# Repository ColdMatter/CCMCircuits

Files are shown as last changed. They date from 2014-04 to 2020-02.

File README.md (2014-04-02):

CCMCircuits
===========

This is a repository for circuits used by the Centre for Cold Matter at Imperial College. Each project should be in its own directory, and should contain a .brd and a .sch file, a "readme.md" file which gives any useful information on the circuit. You can also upload files used to make the circuit in the PCB mill, and any measurements that you make of the circuit's behaviour. Please try not to upload all of the temporary files made by Eagle.

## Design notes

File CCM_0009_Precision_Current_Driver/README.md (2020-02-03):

# Precision Current Driver
     
This is a low-noise, low-current, bipolar-capable precision current supply.  Revision B onwards is modeled after Analog Devices application note AN-968.  Populate components as necessary to produce unipolar/bipolar operation with the desired input voltage to current scaling.

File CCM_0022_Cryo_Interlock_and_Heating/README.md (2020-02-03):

Cryocooler Interlock and Heating
===========

This circuit acts as a control interface and safety interlock for the F50 cryocooler compressor and system heaters for our usual buffer-gas beam configuration of three heater channels.  Both manual or remote control options are available.  The circuit only allows the compressor to be activated if the external (NC) interlock is satisfied.  The initial build of the YbF "box" chamber uses hardware interlocks (in series) on the chamber pressure and temperature of the first and second cooler stages.  Heater control is completely independent of the interlock.  Activation of either the first or second stage (but not the SF6) heaters will disable the cryocooler.

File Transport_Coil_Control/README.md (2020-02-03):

# Transport Coil Control
This is a controlling circuit for the large transport-coil pair used to tranfer CaF molecules from the MOT chamber into the dipole trap / optical tweezers chamber (and potentially also to the chip-trap chamber, the track is certainly long enough!).  We require full control of the coil pair, including the ability to switch between anti-Helmholtz and Helmholtz configurations, as well as the ability to fine tune to position of the field zero (vertically) by shunting current around the coils individually.  A simplified circuit schematic looks as follows.

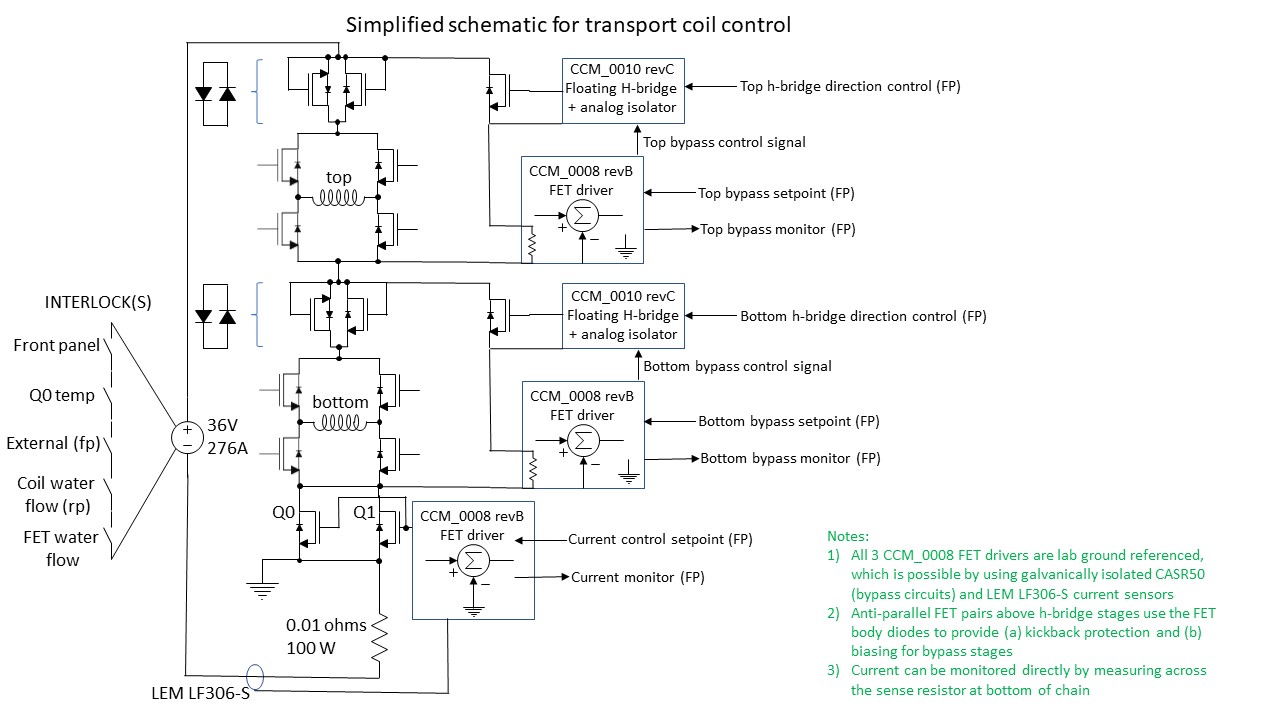
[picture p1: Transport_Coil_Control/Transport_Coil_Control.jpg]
Simplified schematic


Note that the connections to the 8 h-bridge FET gates are not shown.  

## Current sensor and control signal scaling/tuning
The control-voltage to output current conversion is set by adjusting the current monitor (indicator) voltage/current scaling.  The design of the FET-controlling feedback circuit CCM_0008 is such that the control voltage and monitor voltage differ by a factor of 2.  Namely, if the control voltage is 1V/A, the monitor signal will be 0.5V/A.

### Main current path/control
The LEM LF306-S current sensor is a closed-loop Hall sensor that provides a sensor current proportional to the sensed current in the ratio 1:2000.  Explicitly, a 300 A current will give an output of 150 mA.  Using a 33 ohm sense resistor, this gives a sensor voltage of 4.95V/300A.  To get the desired 1V/50A monitor scaling, we need a further gain of 1.212.  The instrumentation amplifier used in the monitor loop is the AD8226, with the gain set according to Rg (kOhms) = 49.4 kOhms / (G-1).  For our desired gain, we need a 232.8 kOhm resistor.  232 kOhms is close enough.  The resulting control voltage to output current scaling differs by a factor of 2, i.e. 1V/25A, or 25A/V.

### Bypass current path/control
The CASR50 sensors used for the two bypass circuits gives an output of 0.625V for the nominal current (50A).  We desire a monitor voltage of 1V/20A, i.e. a 50A bypass current gives a monitor voltage of 2.5V.  Thus, we want gain G = 2.5/0.625 = 4.  To get this gain for the AD8226, the gain resistor should be 16.46 kOhms.  16.5 kOhms is close enough.  The resulting bypass control voltage to output current scaling is half that of the monitor, i.e. 1V/10A, or 10A/V.  

<!-- h<sub>&theta;</sub>(x) = &theta;<sub>o</sub> x + &theta;<sub>1</sub>x -->

## Power supply remote control and monitoring
The current control box includes remote on/off, indicator leds, and signals from the Meanwell RTS-10000-36 high-current supply.  

### Connections and cabling 
The interface to the supply is achieved through three rear-panel connectors called CN991, CN992, and CN993, which are 20 pins, 10 pins, and 10 pins, respectively (HRS DF11-XYDP-2DS connectors, where XY = 10 or 20).  The signals of CN992 and CN993 are connected internally.  I've hacked a commercial DB15 cable to facilitate connecting to the power supply.  The connections are as follows:      

| RTS-10000-36 signal  | rear panel pin | Cable wire color | DB15 position |
| -------------------- | -------------- | ---------------- | ------------- |
| RC+                  | CN992 p10      | pinkish brown    | 1             |
| 12V-AUX              | CN991 p1       | red              | 2             |
| GND-AUX              | CN991 p3       | orange           | 3             |
| DC-OK2               | CN991 p4       | pink             | 4             |
| +V                   | CN991 p5       | yellow           | 5             |
| AC-FAIL2             | CN991 p8       | green            | 6             |
| -V                   | CN991 p7       | cyan             | 7             |
| OTP2                 | CN991 p9       | blue             | 8             |
| FAN-FAIL2            | CN991 p10      | light blue       | 9             |
| OTP1                 | CN991 p13      | purple           | 10            |
| DC-OK1               | CN991 p14      | grey             | 11            |
| AC-FAIL1             | CN991 p19      | white            | 12            |
| FAN-FAIL1            | CN991 p20      | black            | 13            |
| -                    | -              | brown + black    | 14            |
| -                    | -              | red + black      | 15            |
|                      |                |                  |               |

Note that the error/status signals are duplicated in two, electrically independent, channels.  Error signal X1 (e.g. fan-fail1) is a relay contact that closes to indicate failure (connects to fan-fail1-gnd).  Error signal X2 (e.g. fan-fail2) is an open-collector output that accomplishes the same functionality.  I've wired the control box in a way such that either of the two duplicated signals should trigger the indicator led (see below). 

There are also a number of connections to be made locally on the rear panel of the power supply.  Most of these simply connect the status indicator signals to system ground (GND-AUX).  The two exceptions are the output sense feedback, i.e. (CN992 p3 <--> output +) and (CN992 p5 <--> output -).  The ground connections are as follows (local brown wires daisy-chained to GND-AUX on CN991 p3).

| RTS-10000-36 signal  | rear panel pin |
| -------------------- | -------------- |
| RC-                  | CN992 p8       |
| DC-OK2-GND           | CN991 p2       |
| GND-AUX              | CN991 p3       |
| AC-FAIL2-GND         | CN991 p6       |
| OTP2-GND             | CN991 p11      |
| FAN-FAIL2-GND        | CN991 p12      |
| OTP1-GND             | CN991 p15      |
| DC-OK1-GND           | CN991 p16      |
| FAN-FAIL1-GND        | CN991 p18      |
| AC-FAIL1-GND         | CN991 p17      |
|                      |                |

### Remote on/off and interlocks 
The remote on/off control of the power supply is described in its datasheet.  Basically, RC- is connected to GND-AUX and RC+ is connected to 12V-AUX to enable the supply.  We use this as an interlock to enable/disable the supply for water flow and temperature conditions.  All of the following interlocks must be wired closed to enable the supply:

1. Rear panel BNC connector for transport coil water flow and temperature interlock.  If using a polarity-dependent interlock switch (e.g. a FET), the center pin is at higher electrical potential.

2. Front panel BNC connector for optional external interlock.  If using a polarity-dependent interlock switch (e.g. a FET), the center pin is at higher electrical potential.

3. Front panel on/off switch.

4.  Internal cooling water flow (can be manually defeated with internal jumper).  Note that the flow is directional in order to satisfy the interlock.

5. Main controlling FET (parallel pair consisting of Q0/Q1) source-terminal temperature.  Here, we use an AIRPAX normally-closed thermal switch, which opens at approximately 80 C.  

For the flow interlocks, we are currently using the Gems Sensors FS-3 (RS Components #3956940), which closes at a relatively low flow of 0.2 liters/minute.  If any of the interlock conditions are not met, the orange interlock indicator LED on the front panel should illuminate.  The interlock LED driving circuit is as follows.

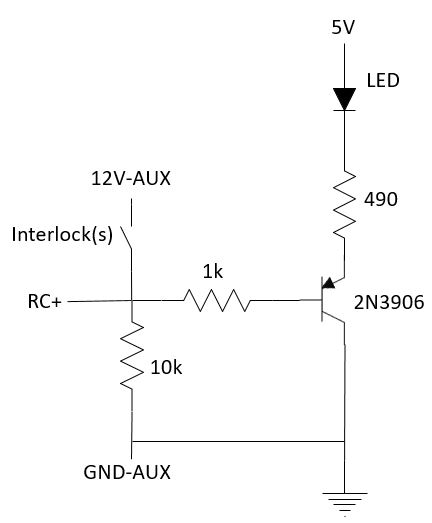
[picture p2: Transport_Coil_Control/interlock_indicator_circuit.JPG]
interlock circuit


### Status indicator leds/circuits
The status signals from the power supply are severly limited in terms of the available output current.  For this reason, I used these signals to drive a few basic transistor circuits that switch the front panel LED indicators on/off.  The LED-drive current itself is derived from the local 5V supply.  The four status indicators are driven by the following circuit.

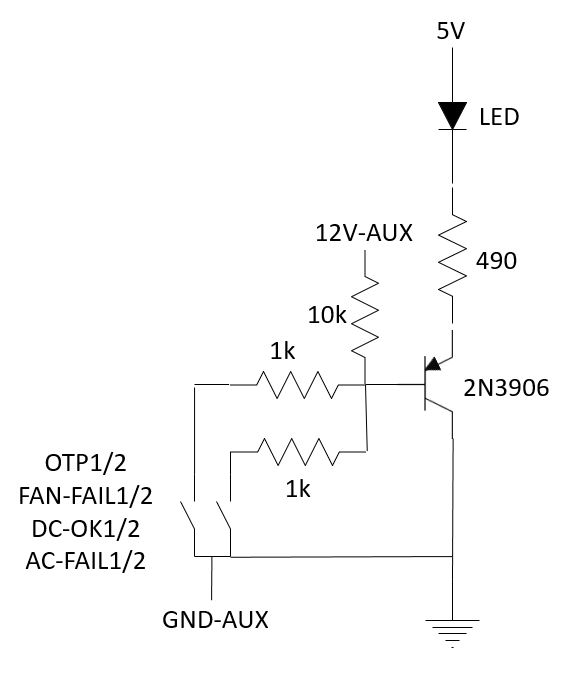
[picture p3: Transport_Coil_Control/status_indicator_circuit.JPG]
status circuit


To indicate a particular status is active, the supply closes an indicator relay that connects the output signal to GND-AUX.  This turns on the pnp BJT ('3906) and activates the LED.  Note that if the supply is not connected, 12V-AUX will not be present and all of the front-panel leds will be lit up.  

## Known Issues

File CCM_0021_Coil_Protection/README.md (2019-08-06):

# CCM_0021 Coil Protection
     
This circuit is designed to provide some level of protection for coils, particularly useful for those installed in vacuum where a melted coil represents a serious annoyance.  It features an adjustable soft current limit (by clamping a control voltage) and an adjustable hard energy limit (by opening an interlock and disabling the power supply).  The latter feature is obtained by integrating the dissipated power (roughly) and comparing to a setpoint.  

## Design Resources

## Design Notes

## Known Issues

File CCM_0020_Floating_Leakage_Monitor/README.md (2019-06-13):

# CCM_0020 50kV Floating pA Leakage Current Monitor
     
This is a circuit used to monitor pA-level leakage currents on the HV plates of 
the ultracold edm experiment.  We have a design goal of having the leakage currents be less than 25 pA.  To make sure this is the case, we want to be able to measure currents at the pA level.  This is hard.  Floating the entire circuit up to a few tens of kV makes it even harder.  This is my kind of problem -NF.    

## Design Resources
- Bob Pease: What's all this teflon stuff anyhow?
- Bob Pease: What's all this femtoampere stuff anyhow?
- Keithley low-level measurement handbook
- LM662 datasheet
- Analog Devices ADA4530-1 datasheet: https://www.analog.com/media/en/technical-documentation/data-sheets/ADA4530-1.pdf 
- Analog Devices ADA4530-1 demo board user's guide: https://www.analog.com/media/en/technical-documentation/user-guides/ADA4530-1R-EBZ_UG-865.pdf

## Design Notes
The transmitter section of the circuit features three critical design elements: 
ultra low input leakage currents, ultra low power consumption, and high voltage 
isolation.  The former is required of any circuit capable of measuring currents 
on the pA level.  The most sensitive way to measure extremely low currents (like the fA-level features by some of the op amps we'll be using here) is to integrate for many seconds and read off the voltage.  Of course, you need an integrating capacitor with low leakage too: a length of teflon coated coaxial wire is a good choice, you can even drive the coax outer conductor with a shielding potential ("self shielded") to avoid dielectric relaxation effects.  The small enclosed volume also lowers the sensitivity to cosmic rays, to which you are sensitive to at this level.  To monitor the leakage on the edm electric field plates, we need a time-resolved signal, so integrating is out.  We don't care at the fA level, so this shouldn't pose a problem.  A sense resistor + buffer amplifier (alternatively, a transimpedance amplifier) should be sensitive enough and give us real-time measurements. 

Achieving ultra low input leakage currents starts with choosing an appropriate 
operational amplifier, in this case in a voltage "buffer" configuration.  Luckily, there are a number of (CMOS) op amps on the market that feature input leakage currents on the order of 10 fA.  We have the additional challenge of needing an op amp that has low quiescent current requirements.  The LMP2231 made by Texas Instruments seems to fit the bill: 20 fA input leakage current (typical, 1 pA max) while only needing 10 uA of quiescent current.

Taking advantage of the ultra-low input current leakage specification of our chosen op amp requires a significant amount of layout/design work.  It won't do us any good to use such an op amp on a dirty FR4 board that will leak currents of many pA into our inputs every time the humidity changes.  The first line of defense is to use a low-leakage circuit board material.  A 4-layer board with outer layers made of Rogers 4350B (a ceramic) and the inner substrate made of FR408 (for strength) seems like a good way to go.  Beyond that, high-impedance circuit inputs are shielded at numerous levels.  The buffer op amp inputs use a "guard ring" driven by a low impedance source (the op amp output) held at the same voltage as the inputs themselves, which eliminates leakage from surrounding on-board potentials.  The guard ring is exposed copper so that no charge carriers can leak past on the soldermask or silkscreen layers.  The guard ring extends underneath the top ceramic layer to shield the input pins (from below) from the FR4 inner layer.  A via fence on the outer perimeter of the guard ring completes the board-level shielding.  Additional shielding is achieved by two layers of brass boxes, the inner one (top and bottom of the board) at the same potential as the guard ring and the outer one (again, on both top and bottom) at floating "ground".  A triax cable uses the same two shielding potentials to bring the HV line into the circuit.

Of all the challenges to overcome here, the HV isolation is perhaps the easiest to overcome.  Optek makes the OPI15X series of opto-couplers/isolators that are rated to 50 kV in air.  We could just do our usual trick: use a sense resistor and buffer amplifier to generate a voltage, convert that voltage to a frequency using a VtoF converter and optically transmit that frequency.  Optical transmission can either be done using a fiber (e.g. Agilent's HFBR-1520) or an Optek OPI155 optoisolator.  However, both of these require significant (many mA) led drive current in order to toggle the logic output on the receiver.  Instead, I'm planning to use the OPI150 optocoupler (transmitting LED + receiving phototransistor) with the phototransistor receiver wired as a photodiode (base shorted to emitter) and the generated photocurrent being detected by a high-gain transimpedance amplifier.  In principle, this should allow us to get the signal out using much less power.  The output of the transimpedance could even feed into a precisely tuned comparator to give high sensitivity and logic-level outputs.  We could even transmit an analog signal instead of a digital one using the same setup but without the receiver comparator.  I think the digital approach will have better noise immunity, larger dynamic range, and potentially uses less power.  That means we'll likely have to do VtoF after all.  Even though you can't buy low power VtoF ICs (or VCOs), you can build your own.  The LTC1541 [op amp + comparator + voltage reference] has one option in the applications section of its datasheet.  You can build a 0-10 kHz VtoF with quiescent current requirements around 5 uA, some 200 x less than the lowest power monolithic solution.  

Along with the problem of high-voltage isolation comes the question of how to power the isolated transmitter section of the circuit.  The most obvious answer is to use batteries, but in practice that turns out to be relatively annoying.  An alternative is to power the circuit using some high-power leds and a solar panel on the transmitter.  This sounds elegant, and I think it probably could be if the transmitter was designed for very low-power operation, but in practice it makes the current monitors very big (and bright -- you need lots of optical power).  I've decided to try something crazy: design for ultra-low power on the transmitter and power it via photocurrent generated from (many of)
the same model of optocoupler that we're using to get the signal out.  With a max allowed LED current of 50 mA and a transfer ratio of ~2000:1, with six optocouplers I think I should be able to create a 2.5 V, 50 uA power supply on the transmitter circuit.  With a careful design I think that should be enough. 

## Known Issues

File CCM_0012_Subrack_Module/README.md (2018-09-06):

# CCM_0012 Subrack Module

This is meant to be the starting point for any circuit/project that will be inserted into a subrack using the standarized CCM bus (see CCM_0011).  Standard board sizes are 160 x 100 mm.

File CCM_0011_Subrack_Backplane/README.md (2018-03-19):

Subrack Backplane
===========
     
This circuit is an attempt to create a subrack standard for CCM circuits.  It uses a 64-pin bus based on the EURO-card standard (100 mm tall boards x various lengths, typically 160 mm) using DIN41612 "Type B" connectors.  The bus provides separate analog and digital ground planes and associated power supplies of +/-15V and +/-5V, respectively.  The backplane provides female connectors with a 4HP pitch.

We have a number of existing circuits that use a 32-pin rear connector (actually a 64-pin connector with half of the pins unpopulated).  The bus standard defined here should be compatible with our existing circuits.

In addition to power rails, the backplane also provides various communication buses, which can be used with microcontroller projects.  Take care though, the GPIOX and ANX lines are shared across all daughter boards, which can cause conflicts if you aren't careful.  In a similar vein, please only install a single power-supply module!

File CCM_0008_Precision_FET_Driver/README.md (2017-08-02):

Coil Driver
===========
     
This circuit provides closed-loop control of either unipolar or bipolar power current-driver output stages.

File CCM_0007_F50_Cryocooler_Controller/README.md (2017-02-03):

Cryocooler Phase Lock
===========

This project is meant to allow us to phase lock our buffer-gas molecular beam experiments to the ~ 1 Hz cryocooler cooling cycle.  It accomplishes this placing a microphone close to the high-pressure helium lines and providing an output trigger based on when the volume exceeds some threshold.  The delay can be controlled with an analog input.

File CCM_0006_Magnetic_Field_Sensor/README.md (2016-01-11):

# CCM_0006 Magnetic field sensor

This is a battery-powered circuit designed to help measure the strong magnetic fields produced by the Zeeman-Sisphus decelerator magnet arrays.  The circuits consists of a single-turn pickup coil (copper trace), and RMS-to-DC converter, summer, and VtoF converter.  The idea is to spin the circuit (using something like the dremmel tool) with the pickup coil in the bore of the magnet arrays.  The LED will flash at a frequency proportional to the field strength and the output signal can be picked up on a photodiode.  Both the rotation rate and magnetic field strength should be able to be derived from the photodiode pickup signal.

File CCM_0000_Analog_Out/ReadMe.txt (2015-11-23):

This is a simple analog output board useful for providing an adjustable voltage to a pzt amplifier, cavity, etc.  Jumpers allow the user to choose between unipolar and bipolar operation.  Substituting various LM-4040 (or equivalent) reference diodes allows the voltage ranges to be adjusted.  

Currently, everyone in the lab uses 9V batteries with old-school trimpots wired up to them for this type of application.  Unsurprisingly, nobody ever remembers to disconnect the battery when they are finished.  As a result, we have lots of dead 9V batteries in the lab.  I've remedied the problem temporarily with some rechargeable batteries, but the practice is still stupid.

It might be a better idea to do a multi-channel board that fits nicely in a NIM rack...

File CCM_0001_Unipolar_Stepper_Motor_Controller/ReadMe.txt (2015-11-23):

To configure a blank board, flash the PIC and run the FTDI chip configure batch file/utility (ftdi/stepper_ftdi_config.bat).

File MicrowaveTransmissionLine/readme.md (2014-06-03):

Microwave transmission line		
=====================
A short section of 50 ohm parallel plate transmission line for 14.5GHz microwaves, with two feedthroughs.

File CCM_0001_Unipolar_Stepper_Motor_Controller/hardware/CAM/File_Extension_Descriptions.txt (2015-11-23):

Extension Description

.cmp copper top (component) side
.drd	drill 
.dri drill station info
.gpi photoplotter info file
.plc silk screen top (component) side
.pls silk screen bottom (solder) side
.sol copper bottom (solder) side
.stb stencil file bottom (solder) side
.stc solder stop mask top (component) side
.sts solder stop mask bottom (solder) side
.stt stencil file top (component) side

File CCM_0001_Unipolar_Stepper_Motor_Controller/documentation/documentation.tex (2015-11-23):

\documentclass[10pt]{article}
\usepackage{amsmath,graphicx,xcolor,tikz,amssymb,multirow}
\usepackage[final]{pdfpages}
\usepackage{hyperref}
\usepackage{empheq}
\usepackage{fancyhdr}
\usepackage{textcomp}
\usepackage{placeins}
\usepackage{url}

\newcommand{\HRule}{\rule{\linewidth}{0.5mm}}

\newcommand{\comm}[3]{
\nonumber \textcolor{red}{?} \, \textcolor{blue}{!} \, \textcolor{red}{\text{ #1}} \,\textcolor{red}{\text{#2, }} \, \textcolor{blue}{\text{AOK.}} \, & \text{\hspace{0.5in}#3}}

\newcommand{\exchange}[2]{
\begin{equation}
 \nonumber \textcolor{red}{?} \, \textcolor{blue}{!} \, \textcolor{red}{\text { #1}} \,\textcolor{red}{\text{#2, }} \, \textcolor{blue}{\text{AOK.}}
 \end{equation}
}

\newcommand{\exchangeWithData}[2]{
\begin{equation}
 \nonumber \textcolor{red}{?} \, \textcolor{blue}{!} \, \textcolor{red}{\text { #1}} \,\textcolor{red}{\text{#2, }} \, \textcolor{blue}{data1,data2,...} \, \textcolor{blue}{AOK.}
 \end{equation}
}

\pagestyle{fancy}
\lhead{{\large Stepper Motor Controller}}
\rhead{}
\chead{}
\lfoot{{\large Imperial College CCM \the\year}}
\rfoot{\large Page \thepage}
\cfoot{}
\setlength{\headheight}{14pt} 
\renewcommand{\headrulewidth}{0.4pt}
\renewcommand{\footrulewidth}{0.4pt}

\begin{document}
\input{./title.tex}

\newpage
\tableofcontents

\newpage
{\large{\bf Known Issues}}
\begin{enumerate}
\item{Somehow I forgot to put a pullup resistor on the $\overline{\text{MCLR}}$ line of the PIC.  In order to operate, put a 10k$\Omega$ pullup resistor to 5V.  Just under the programming connector is a convenient place (0603/0805 between that and the adjacent pin).}
\end{enumerate}

\vspace{0.5in}

{\large{\bf Minimum Requirements}}
\begin{enumerate}
\item{If using the provided GUI, you will need windows XP or newer (system has only tested on Windows 7).}
\item{If PC control/interaction with the controller is desired, you must at the very least have the FTDI COM port drivers installed.  These are included in the gui installation executable.}
\end{enumerate}

\FloatBarrier
\newpage
%%%%%%%%%%%%%%%%%%%%%%%%%%%%%%%%%%%%%%%%%%%%%%%%%%%%%%
%%%%%%%%%%%%%%%%%%%%%%%%%%%%%%%%%%%%%%%%%%%%%%%%%%%%%%%
\section{System Overview}
This circuit and associated firmware/software act as a controller for a standard unipolar (6 wire) stepper motor.  The rotary position of the motor can be controlled from a usb connection using a simple serial protocol, or with the provided gui.  In addition, a number of potentially useful predefined operation modes are available for controlling the motor.  The hardware also includes a rotation sensor, making possible both open and closed-loop operation.

All files and folders discussed in this documentation are located in the \url{CCM_0001_Unipolar_Stepper_Motor_Controller\\RevA} directory.  File and folder paths referenced herein are described \emph{relative} to this location.

%%%%%%%%%%%%%%%%%%%%%%%
\subsection{Hardware}
\label{Hardware}   
The heart of the controller is a PIC18F46K80, with a number of peripherals to facilitate motor control.  These include a DS3231M real time clock, 24AA1025 external eeprom, HCTL-2021 quadrature encoder, AMT102 rotation sensor, L297 motor driver, and power FETs for the output drive stages.  Two external bnc inputs (trigger and direction control) and two pushbuttons facilitate control of the motor by the user in various operation modes.  An LCD screen provides visual feedback of motor behaviour to the user. 

The motor used for the purpose of this documentation, and that which was used in the initial builds of the prototype circuits, is part number 191-8299 from RS components.  This is a 12V, 0.4A/phase 1.8$^\circ$/step motor.  The motor runs quite hot when supplied with the full specified voltage, for this reason the prototypes were built using a 7.5V supply instead.  The lower supply voltage sacrifices a bit of switching speed and torque but otherwise has no adverse consequences.  With these operating parameters, the fasted stepping rate is on the order of 500 Hz.  Stepping speed performance and reliability is load dependent and should be tested for the particular applications.         

%%%%%%%%%%%%%%%%%%%%%%%
\subsection{Open vs. Closed Loop Operation}
\label{Open_vs_Closed} 
Although probably not needed for most applications, the controller can be operated in closed-loop mode.  When operated this way, the current position of the motor is determined by the AMT-102 rotation sensor, rather than by how many steps the controller has instructed it to take.\footnote{The rotation sensor is set to output 800 quadrature encoded pulses per rotation.  The quadrature encoder used multiplies this by 4 so we get 16 counts for every step of the motor.}  When operated closed-loop, the controller will attempt to make this position equal to the desired position (determined by the number of triggers received in external mode, or where it thinks the motor should be in other modes).  Closed-loop operation will probably be most useful in situations where the load torque is significant, which can cause the stepping motor to ``slip'', i.e. not actually take a step even though the controlling currents toggled correctly.  If it is crucial that the motor position be accurate, it is recommended to use closed-loop mode.    

\FloatBarrier
\newpage
%%%%%%%%%%%%%%%%%%%%%%%%%%%%%%%%%%%%%%%%%%%%%%%%%%%%%%%%%
%%%%%%%%%%%%%%%%%%%%%%%%%%%%%%%%%%%%%%%%%%%%%%%%%%%%%%%%%
\section{GUI} 
\label{GUI}    

In addition to the developed firmware and hardware, there is also a provided GUI that facilitates control of the motor position and configuration of the predefined operation modes.  The GUI itself was written in Labview, which is horrible of me I know.  However, this was based on an old project and I didn't see the value in re-inventing the wheel there.    

The controller system can be installed by running
\url{gui\\Installer_Builds\\Volume\\setup.exe}.  This will carry out installation of the gui, FTDI device drivers, and Labview runtime engine.  A shortcut to the gui executable will be created on your desktop.  Updates of the gui can be carried out by simply replacing the executable itself, there is no need to rerun the entire installer.

When the gui executable is run, the first thing the back end code will do is search for a controller on the specified COM port.  The result of this test is indicated with the ``Controller Detected?'' LED.  Each time a button is depressed, and an action is taken, the ``Task Completed?'' LED will indicate the success (or lack thereof) of carrying out the desired operation.  For tasks that take a long time to execute, such as a goto, this LED will blink yellow while the task is carried out.  Explicit views of the data sent to and returned from the controller are shown in the two boxes to the left of the tab control.  Responses of AOK typically indicates the command was received and executed successfully.  ERR will indicate there was an error.  

%%%%%%%%%%%%%%%%%%%%%%%%%%%%%%%%%
\subsection{Basic Operation}
\label{Basic_Operation}
The basic operation tab of the controller gui allows for immediate control of the motor position (goto/move) as well as setting a number of operation variables.  These include uploading the current time, setting position limits, step rates, etc.    

\begin{figure}[!htb]
\centering
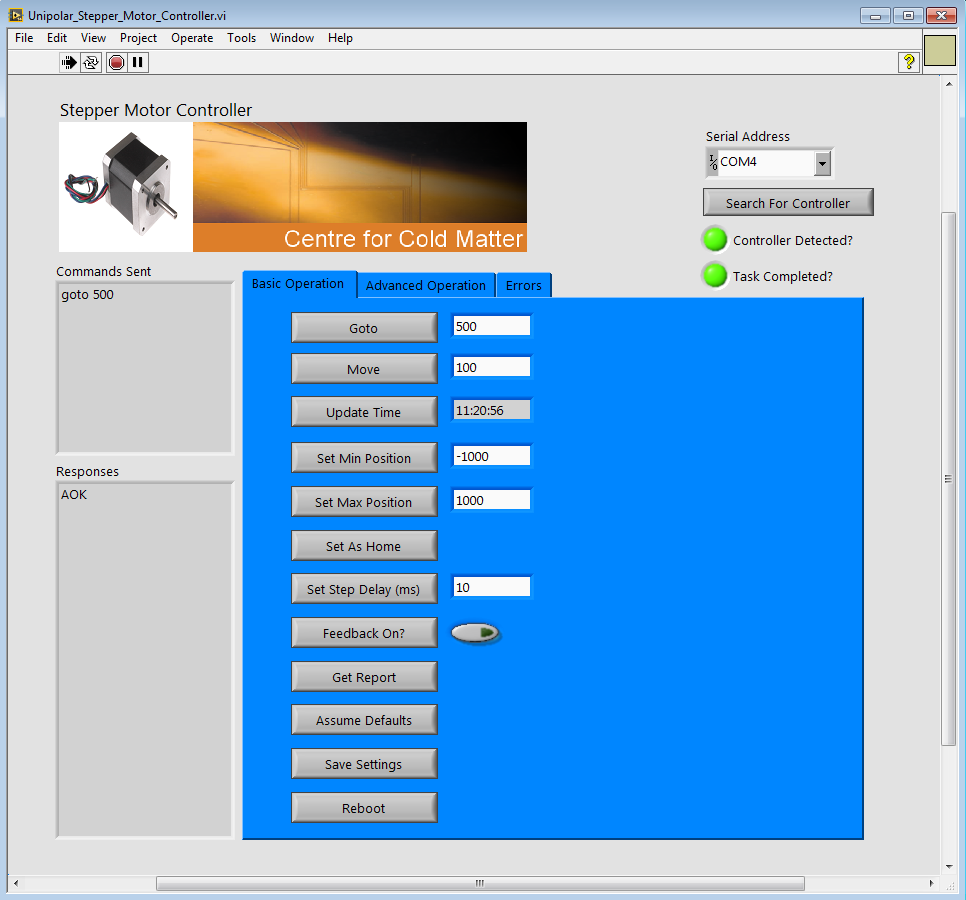
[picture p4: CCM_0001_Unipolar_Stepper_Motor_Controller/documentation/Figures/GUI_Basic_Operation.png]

\caption{Basic operation tab of the motor controller gui.}
\label{GUI_Basic_Operation}
\end{figure} 

\FloatBarrier
%%%%%%%%%%%%%%%%%%%%%%%%%%%%%%%%%
\subsection{Advanced Operation}
\label{Advanced_Operation}

The advanced operation tab (see Figure \ref{GUI_Advanced_Operation}) of the gui is used to configure the predefined operation modes native to the controller firmware.  Various configuration settings will be enabled/disabled, depending on the operation mode selected in the top dropdown menu.  The sequence of serial commands sent to the controller to configure the mode (in the Figure the triggered-goto mode has just been configured) is explained in detail in Section \ref{Configuring_Predefined_Operation_Modes}.  

\begin{figure}[!htb]
\centering
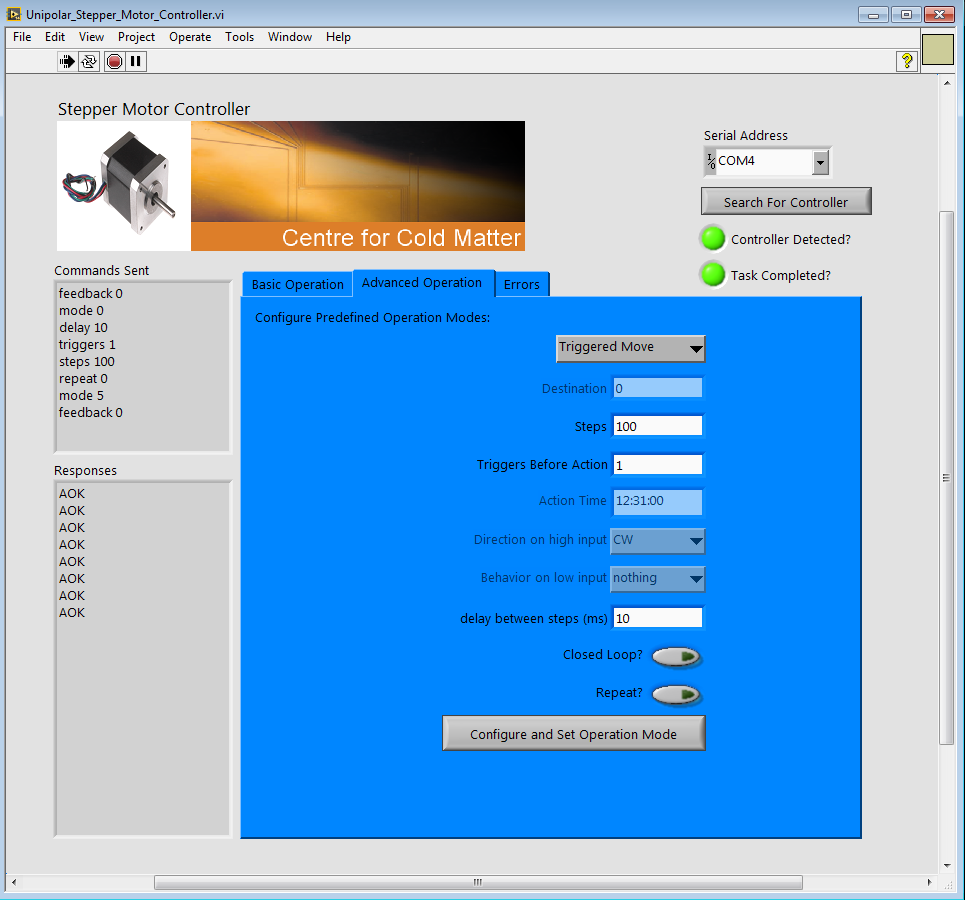
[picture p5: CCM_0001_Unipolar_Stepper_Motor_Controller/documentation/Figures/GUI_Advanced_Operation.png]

\caption{Advanced operation tab of the motor controller gui, used for configuring the predefined modes of operation.}
\label{GUI_Advanced_Operation}
\end{figure}

\subsubsection{Motor Disabled (0)}
In this mode the motor is disabled (stepping currents are turned off), allowing for free rotation.  

\subsubsection{Manual (1)}
In manual mode, the position of the motor is controlled using the two front-panel pushbuttons.  Push once to step the motor once, push and hold to continually rotate the motor.  

\subsubsection{External (2)}
In external mode, the stepping rate and direction of the motor are controlled by the two bnc inputs,  steps being taken on rising edges of the trigger input.  At the time of the rising edge of the trigger, the direction logic level determines if a positive (1) or negative (0) step is to be taken.  The direction logic input should be stable for at least $\pm$10$\mu$s around the rising trigger edge.  

\subsubsection{Triggered Goto (3)}
In triggered-goto mode, the controller is loaded with a goto destination and required number of triggers.  It then counts incoming triggers on the external bnc input (rising edges), the goto being completed when the desired number of triggers has been reached.  After completion, the controller automatically assumes manual mode.      

\subsubsection{Timed Goto (4)}
In timed-goto mode, the controller is loaded with a goto destination and action time.  The current time is monitored until a match is detected for hours/minutes/seconds, at which point the goto is completed.  After completion, the controller automatically assumes manual mode.  

\subsubsection{Triggered Move (5)}
In triggered-move mode, the controller is loaded with a step value and required number of triggers.  It then counts incoming triggers on the external bnc input (rising edges), the move being completed when the desired number of triggers has been reached.  Behaviour after the move is determined by the ``repeat'' setting.  If true, the controller resets the trigger count and prepares to repeat the move procedure once the required number of triggers has again been reached.  If false, the controller assumes the manual operation mode.  

\subsubsection{Timed Move (6)}
In timed-move mode, the controller is loaded with a step value and action time.  The current time is monitored until a match is detected for hours/minutes/seconds, at which point the move is completed.  Behaviour after the move is determined by the ``repeat'' setting.  If true, the controller resets the trigger count and prepares to repeat the move procedure once the required number of triggers has again been reached.  If false, the controller assumes the manual operation mode.

\subsubsection{State-Based Rotation (7)}
In state-rotation mode, the controller continually rotates the motor.  The rotation direction is determined by the instantaneous state of the external ``trigger'' bnc input and the ``rotate'' and ``behave'' settings, as summarized in Table \ref{State_Rotate_Table}.  When the external trigger input is high, the rotation direction is determined by the rotate setting.  When low, the motor can either do nothing (behave=0), or anti-rotate (behave=1) against the normal ``external trigger is high'' direction.  No feedback is possible during this mode.    

\begin{table}
\centering
\begin{tabular}{|c|c|c|c|}
\hline
Ext Trigger & rotate & behave & motion \\
\hline
1 & 0 & - & negative rotation \\
\hline
1 & 1 & - & positive rotation \\
\hline
0 & - & 0 & no motion \\
\hline
0 & - & 1 & anti-rotate ($\overline{\text{rotate}}$)  \\
\hline
\end{tabular}
\caption{Motor control in the ``state rotate'' operation mode is controlled by a single external input (Ext Trigger) and two internally set bits (rotate and behave).}
\label{State_Rotate_Table}
\end{table}  

\subsubsection{Triggered Shutter (8)}
In the triggered-shutter mode, the controller waits for a number of triggers (rising edges on the external trigger input) before moving the motor a specified number of steps, in effect ``opening'' a shutter.  The controller then resets the trigger count and waits for the same number of triggers before returning to the home position.  This mode repeats indefinitely.  

\subsubsection{State Shutter (9)}
In the state-shutter mode, the controller monitors the external trigger input and positions the motor in one of two places depending on the current logic state.  The direction and rotation amplitude is set by the ``steps'' variable.  This mode repeats indefinitely.  

\FloatBarrier
\newpage
%%%%%%%%%%%%%%%%%%%%%%%%%%%%%%%%%%%%%%%%%%%%%%%%%%%%%%%%%
%%%%%%%%%%%%%%%%%%%%%%%%%%%%%%%%%%%%%%%%%%%%%%%%%%%%%%%%%
\section{Serial Communication} 
\label{Serial_Communication}
In addition to the GUI, general operation and configuration of the individual predefined operation modes can be configured directly over a serial port connection.  This project uses a baud rate of 4800, 8 data bits, 1 stop bit, no port control, and no parity bit.

Each exchange between the host (PC) and the controller consists of the host giving the controller a task.  Task-dependent behaviour, including exchange of data or changing settings, can then take place.  The assignment and carrying out of each task follows a fixed protocol, as summarized in the following list. For clarity of discussion regarding communication between the host and controller, \textcolor{red}{red characters/data are sent from the host to the controller} and  \textcolor{blue}{blue characters/data are sent from the controller to the host}.   
  
\begin{enumerate}
\item{The wakeup ascii character \textcolor{red}{?} is sent to the controller to instigate communication.}
\item{When ready to receive the command, the controller returns \textcolor{blue}{!}.  If the wakeup characters was incorrect, the controller returns \textcolor{blue}{?} instead and aborts the operation.}
\item{The command, with required arguments, is sent to the controller.  If a command has arguments, the command and it's arguments are separated by a space.  The command/argument sequence terminates with a carriage return ascii character (CR, 0x13) or line feed (LF, 0x10).\footnote{Technically, \emph{any} non-alphabetic or numeric ascii character will work, other than a space.}}
\item{The controller carries out the specified task.}
\item{The controller ends the current task by sending "AOK" if the task was carried out without errors, or "ERR" if an error occurred, potentially with an error message, terminated by a line feed (LF, 0x10).}
\end{enumerate}

An example of adjusting settings on the controller from a serial port terminal (TeraTerm in this case) is shown in Figure \ref{Serial_Example}.  The terminal is setup to echo host keyboard entries to the screen.  As shown, each command begins with the exchange of ``?'' (sent by the host), with ``!'' returned from the controller.    

\begin{figure}[!htb]
\centering
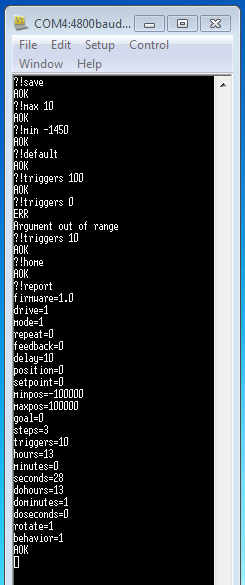
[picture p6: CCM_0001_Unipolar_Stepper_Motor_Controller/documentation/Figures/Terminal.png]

\caption{Example interaction with the controller over USB using individual commands sent from teraterm.}
\label{Serial_Example}
\end{figure} 

\FloatBarrier
%%%%%%%%%%%%%%%%%%%%%%%%%%%%%%%%%%%%%%%%%%
\subsection{Available Commands}

Available commands sent to the controller and brief description of the associated task are summarized in Table \ref{commands}.  The ``goto'' and ``move'' commands are used for immediate motor operation.  Some of the other commands are only used in certain operation modes.        

\begin{table}[!hb]
\centering
\begin{tabular}{|c|c|c|}
\hline
Command & 
Description & 
used in modes 
\\
\hline
\hyperref[report]{report} & 
report current settings &
-
\\ \hline
\hyperref[default]{default} & 
assume default values &
-
\\ \hline
\hyperref[save]{save} & 
save settings &
-
\\ \hline
\hyperref[home]{home} & 
set position as home &
-
\\ \hline
\hyperref[reboot]{reboot} & 
reboot the controller &
-
%\\ \hline
%\hyperref[update]{update} & 
%update firmware &
%-
\\ \hline
\hyperref[move]{move} & 
move the motor N steps &
-
\\ \hline
\hyperref[goto]{goto} & 
goto position &
-
\\ \hline
\hyperref[max]{max} & 
set maximum position &
all
\\ \hline
\hyperref[min]{min} & 
set minimum position &
all
\\ \hline
\hyperref[delay]{delay} & 
set delay between steps &
all
\\ \hline
\hyperref[feedback]{feedback} & 
set feedback on/off &
all
\\ \hline
\hyperref[mode]{mode} & 
set operation mode &
-
\\ \hline
\hyperref[steps]{steps} & 
set number of steps &
5,6,8,9
\\ \hline
\hyperref[triggers]{triggers} & 
set trigger events before action&
3,5,8
\\ \hline
\hyperref[goal]{goal} & 
set destination &
3,4
\\ \hline
\hyperref[hours]{hours} & 
set current time (hours) &
4,6
\\ \hline
\hyperref[minutes]{minutes} & 
set current time (minutes) &
4,6
\\ \hline
\hyperref[seconds]{seconds} & 
set current time (seconds) &
4,6
\\ \hline
\hyperref[dohours]{dohours} & 
set action time (hours) &
4,6
\\ \hline
\hyperref[dominutes]{dominutes} & 
set action time (minutes) &
4,6
\\ \hline
\hyperref[doseconds]{doseconds} & 
set action time (seconds) &
4,6
\\ \hline
\hyperref[repeat]{repeat} & 
set loop behaviour condition &
5,6
\\ \hline
\hyperref[rotate]{rotate} & 
set rotation direction for logic high input &
7
\\ \hline
\hyperref[behave]{behave} & 
set state-rotate behaviour for logic low input &
7
\\ \hline
\end{tabular}
\caption{Available commands to send to the controller from the host.}
\label{commands}
\end{table} 

Examples of the usage of each command in Table \ref{commands} appears below.  Some commands require arguments, while others do not.
In each example, commas (,) indicate carriage returns and periods (.) indicate line feeds.  

%%%%%%%%%%%%%%%%%%%%%%%%%
\subsubsection{report}
\label{report}
Instructs the controller to return a list of the current settings, each setting is of the format ``setting$=$value'', with a carriage return between each list entry. 

\exchangeWithData{report}{} 

%%%%%%%%%%%%%%%%%%%%%%%%%
\subsubsection{default}
\label{default}
Instructs the controller to restore default values. 

\exchange{default}{}

%%%%%%%%%%%%%%%%%%%%%%%%%
\subsubsection{save}
\label{save}
Instructs the controller to save the current settings.  These will be restored if the controller is reset.

\exchange{save}{}

%%%%%%%%%%%%%%%%%%%%%%%%%
\subsubsection{home}
\label{home} 
Instructs the controller to set the current position as home (0).

\exchange{home}{}
    
%%%%%%%%%%%%%%%%%%%%%%%%%
\subsubsection{reboot}
\label{reboot}
Carries out a restart of the controller equivalent to that during a hard power supply cycle.  The communication flow looks like:    

\exchange{reboot}{}

%%%%%%%%%%%%%%%%%%%%%%%%%
%\subsubsection{update}
%\label{update}
%Invokes the bootloader on the controller, in order to carry out a firmware update.  %This should be used in conjunction with the ds30 bootloader utilities, available in %the \url{bootloader\\ds30} directory.  The communication flow follows:    

%\exchange{update}{}

%%%%%%%%%%%%%%%%%%%%%%%%%
\subsubsection{move}
\label{move}
Moves the motor a specified number of steps. The number of steps must be between -2000000 and 2000000.         

\exchange{move}{-100}

%%%%%%%%%%%%%%%%%%%%%%%%%
\subsubsection{goto}
\label{goto}
Moves the motor to a specified position. The destination must be between -1000000 and 1000000.         

\exchange{goto}{1000}

%%%%%%%%%%%%%%%%%%%%%%%%%
\subsubsection{max}
\label{max}
Set the maximum allowed motor position, -1000000 to 1000000.         

\exchange{max}{10000}

%%%%%%%%%%%%%%%%%%%%%%%%%
\subsubsection{min}
\label{min}
Set the minimum allowed motor position, -1000000 to 1000000.         

\exchange{min}{-10000}

%%%%%%%%%%%%%%%%%%%%%%%%%
\subsubsection{delay}
\label{delay}
Set the approximate delay time between steps (for moves, gotos, etc.), 10-65535 (ms).         This is not a guaranteed timescale, the user should test for themselves if precise timing is required. 

\exchange{delay}{10}

%%%%%%%%%%%%%%%%%%%%%%%%%
\subsubsection{feedback}
\label{feedback}
Instructs the controller to turn the feedback off (0) or on (1). 

\exchange{feedback}{0}

%%%%%%%%%%%%%%%%%%%%%%%%%
\subsubsection{mode}
\label{mode}
Set the operation mode, as summarized in Table \ref{Operation_Modes_Table}.  The destination mode should be fully configured before transferring.   

\exchange{mode}{1}

\begin{table}[!htb]
\centering
\begin{tabular}{|c|c|c|}
\hline
Mode & Behaviour \\ \hline
0 & motor disabled \\ \hline
1 & manual \\ \hline
2 & external \\ \hline
3 & triggered goto \\ \hline
4 & timed goto \\\hline
5 & triggered move \\ \hline
6 & timed move \\ \hline
7 & state-based rotation \\ \hline
8 & triggered shutter \\ \hline
9 & state-based shutter \\ \hline
\end{tabular}
\caption{Pre-defined operation modes.}
\label{Operation_Modes_Table}
\end{table}

%%%%%%%%%%%%%%%%%%%%%%%%%
\subsubsection{steps}
\label{steps}
Set the number of steps, -2000000 to 2000000.  Used to configure various predefined operation modes (shutter and move modes).

\exchange{steps}{87}

%%%%%%%%%%%%%%%%%%%%%%%%%
\subsubsection{triggers}
\label{triggers}
Set the number of triggers (rising edges on external trigger input) before action is to be taken.  The allowed range is 1-65535.  This parameter is used for various predefined operation modes.

\exchange{triggers}{10}

%%%%%%%%%%%%%%%%%%%%%%%%%
\subsubsection{goal}
\label{goal}
Set the destination for goto-style predefined operation modes.

\exchange{goal}{-145}

%%%%%%%%%%%%%%%%%%%%%%%%%
\subsubsection{hours}
\label{hours}
Set the current time (hours, 0-23).  Used for time-dependent operation modes.

\exchange{hours}{12}

%%%%%%%%%%%%%%%%%%%%%%%%%
\subsubsection{minutes}
\label{minutes}
Set the current time (minutes, 0-59). Used for time-dependent operation modes.

\exchange{minutes}{30}

%%%%%%%%%%%%%%%%%%%%%%%%%
\subsubsection{seconds}
\label{seconds}
Set the current time (seconds, 0-59). Used for time-dependent operation modes.

\exchange{seconds}{30}

%%%%%%%%%%%%%%%%%%%%%%%%%
\subsubsection{dohours}
\label{dohours}
Set the action time (hours, 0-23).  Used for time-dependent operation modes.

\exchange{dohours}{12}

%%%%%%%%%%%%%%%%%%%%%%%%%
\subsubsection{dominutes}
\label{dominutes}
Set the action time (minutes, 0-59). Used for time-dependent operation modes.

\exchange{dominutes}{30}

%%%%%%%%%%%%%%%%%%%%%%%%%
\subsubsection{doseconds}
\label{doseconds}
Set the action time (seconds, 0-59). Used for time-dependent operation modes.

\exchange{doseconds}{30}

%%%%%%%%%%%%%%%%%%%%%%%%%
\subsubsection{repeat}
\label{repeat}
Set the repetition behaviour for various operation modes, such as a triggered move. If turned off (0), after the move is completed, the operation mode will be set to manual.  If turned on (1), the mode will remain unchanged and the desired operation will repeat again once the necessary conditions are met (triggers received or time-of-day match etc.). 

\exchange{repeat}{1}

%%%%%%%%%%%%%%%%%%%%%%%%%
\subsubsection{rotate}
\label{rotate}
Used for rotate mode.  Instructs the motor which way to rotate for a logic high on the external trigger input.   

\exchange{rotate}{1}

%%%%%%%%%%%%%%%%%%%%%%%%%
\subsubsection{behave}
\label{behave}
Set the rotation behaviour in the state-rotate mode when the external trigger bnc input is logic low.  If 0, the motor does nothing for a logic-low input.  If 1, the motor anti-rotates in the direction opposite of that determined by the ``rotate'' setting. 

\exchange{behave}{0} 

%%%%%%%%%%%%%%%%%%%%%%%%%%%%%%%%%%%%%%%%%%
\subsection{Configuring Predefined Operation Modes via USB}
\label{Configuring_Predefined_Operation_Modes}
Configuring the predefined operation modes over USB, rather than the GUI, consists of completing a sequence of exchanges with the controller.  It is recommended that when configuring a mode, the first few commands disable the motor and turn the feedback off.  This will ensure that the subsequent commands, used to configure the mode, can be carried out without the motor undergoing uncontrolled motion.  If removing the motor drive during configuration is a concern, the manual mode of operation can be assumed instead.  Examples of configuring each mode using the serial port follow.  Some settings will not need to be configured separately for each mode as shown, depending on the values before configuration.    

\subsubsection{Configuring ``Off'' Mode}
\begin{align}
\comm{feedback}{0}{disable feedback} \\
\comm{mode}{0}{disable motor} \\
\nonumber
\end{align}

\subsubsection{Configuring ``Manual'' Mode}
\begin{align}
\comm{feedback}{0}{disable feedback} \\
\comm{mode}{0}{disable motor} \\
\comm{delay}{x}{set delay between steps} \\
\comm{mode}{1}{set mode to manual} \\
\comm{feedback}{1}{turn feedback on (if desired)} \\
\nonumber
\end{align}

\subsubsection{Configuring ``External'' Mode}
\begin{align}
\comm{feedback}{0}{disable feedback} \\
\comm{mode}{0}{disable motor} \\
\comm{mode}{2}{set mode to external} \\
\comm{feedback}{1}{turn feedback on (if desired)} \\
\nonumber
\end{align}

\subsubsection{Configuring ``Triggered Goto'' Mode}
\begin{align}
\comm{feedback}{0}{disable feedback} \\
\comm{mode}{0}{disable motor} \\
\comm{delay}{a}{set delay between steps, ms (a)} \\
\comm{triggers}{b}{set number of triggers before goto completed (b)} \\
\comm{goal}{c}{set destination position (c)} \\
\comm{mode}{3}{set mode to triggered goto} \\
\comm{feedback}{1}{turn feedback on (if desired)} \\
\nonumber
\end{align}

\subsubsection{Configuring ``Timed Goto'' Mode}
\begin{align}
\comm{feedback}{0}{disable feedback} \\
\comm{mode}{0}{disable motor} \\
\comm{delay}{a}{set delay between steps, ms (a)} \\
\comm{hours}{b}{set current time, hours (b)} \\
\comm{minutes}{c}{set current time, minutes (c)} \\
\comm{seconds}{d}{set current time, seconds (d)} \\
\comm{dohours}{e}{set action time, hours (e)} \\
\comm{dominutes}{f}{set action time, minutes (f)} \\
\comm{doseconds}{g}{set action time, seconds (g)} \\
\comm{goal}{h}{set destination position (h)} \\
\comm{mode}{4}{set mode to timed goto} \\
\comm{feedback}{1}{turn feedback on (if desired)} \\
\nonumber
\end{align}

\subsubsection{Configuring ``Triggered Move'' Mode}
\begin{align}
\comm{feedback}{0}{disable feedback} \\
\comm{mode}{0}{disable motor} \\
\comm{delay}{a}{set delay between steps, ms (a)} \\
\comm{triggers}{b}{set number of triggers before goto completed (b)} \\
\comm{steps}{c}{set number of steps to take (c)} \\
\comm{mode}{5}{set mode to triggered move} \\
\comm{feedback}{1}{turn feedback on (if desired)} \\
\nonumber
\end{align}

\subsubsection{Configuring ``Timed Move'' Mode}
\begin{align}
\comm{feedback}{0}{disable feedback} \\
\comm{mode}{0}{disable motor} \\
\comm{delay}{a}{set delay between steps, ms (a)} \\
\comm{hours}{b}{set current time, hours (b)} \\
\comm{minutes}{c}{set current time, minutes (c)} \\
\comm{seconds}{d}{set current time, seconds (d)} \\
\comm{dohours}{e}{set action time, hours (e)} \\
\comm{dominutes}{f}{set action time, minutes (f)} \\
\comm{doseconds}{g}{set action time, seconds (g)} \\
\comm{steps}{h}{set number of steps to take (h)} \\
\comm{mode}{6}{set mode to timed move} \\
\comm{feedback}{1}{turn feedback on (if desired)} \\
\nonumber
\end{align}

\subsubsection{Configuring ``State Rotate'' Mode}
\begin{align}
\comm{feedback}{0}{disable feedback} \\
\comm{mode}{0}{disable motor} \\
\comm{delay}{a}{set delay between steps, ms (a)} \\
\comm{rotate}{b}{set direction to rotate on high input (b)} \\
\comm{behave}{c}{set behaviour on low input (c)} \\
\comm{mode}{7}{set mode to state rotate} \\
\nonumber
\end{align}

\subsubsection{Configuring ``Triggered Shutter'' Mode}
\begin{align}
\comm{feedback}{0}{disable feedback} \\
\comm{mode}{0}{disable motor} \\
\comm{delay}{a}{set delay between steps, ms (a)} \\
\comm{triggers}{b}{set trigger number for opening/closing (b)} \\
\comm{steps}{c}{set number of steps to take (c)} \\
\comm{mode}{8}{set mode to triggered shutter} \\
\comm{feedback}{1}{turn feedback on (if desired)} \\
\nonumber
\end{align}

\subsubsection{Configuring ``State Shutter'' Mode}
\begin{align}
\comm{feedback}{0}{disable feedback} \\
\comm{mode}{0}{disable motor} \\
\comm{delay}{a}{set delay between steps, ms (a)} \\
\comm{steps}{b}{set number of steps to take (b)} \\
\comm{mode}{9}{set mode to state shutter} \\
\comm{feedback}{1}{turn feedback on (if desired)} \\
\nonumber
\end{align}

\newpage
\FloatBarrier
%%%%%%%%%%%%%%%%%%%%%%%%%%%%%%%%%%%%%%%%%%%%%%%   
%%%%%%%%%%%%%%%%%%%%%%%%%%%%%%%%%%%%%%%%%%%%%%%
\section{Prototype Builds}
\label{Prototype_Builds} 

\newpage
\FloatBarrier
%%%%%%%%%%%%%%%%%%%%%%%%%%%%%%%%%%%%%%%%%%%%%%%   
%%%%%%%%%%%%%%%%%%%%%%%%%%%%%%%%%%%%%%%%%%%%%%%
\section{Circuit Schematics}
\label{Circuit_Schematics}    

\includepdf			
[pages=-,angle=90,pagecommand={},width=6.5in,height=9in]
{Figures/CCM_0001.pdf}

\end{document}

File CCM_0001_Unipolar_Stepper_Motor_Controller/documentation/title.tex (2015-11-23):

\begin{titlepage}
\begin{center}

% Upper part of the page. The '~' is needed because \\
% only works if a paragraph has started.
%\includegraphics[width=0.75\textwidth]{./Figures/AO_3.png}~\\[1cm]

% Title
\HRule \\[0.4cm]
{ \huge \bfseries Stepper Motor Controller \\[0.4cm] }

\textsc{\Large RevA}\\[0.5cm]
\textsc{\Large Center for Cold Matter}\\[0.5cm]

\HRule \\[1.5cm]

\centering
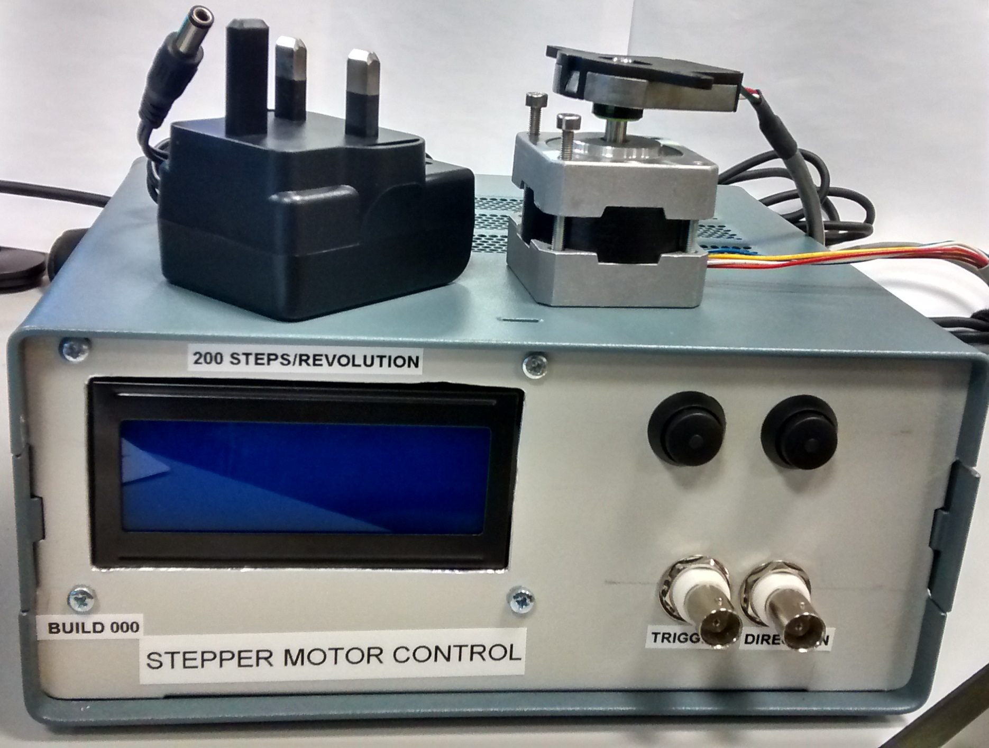
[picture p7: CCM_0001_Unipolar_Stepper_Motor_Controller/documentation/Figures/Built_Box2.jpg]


\vfill

% Bottom of the page
{\large Noah Fitch} \\
{\large \today}

\end{center}
\end{titlepage}

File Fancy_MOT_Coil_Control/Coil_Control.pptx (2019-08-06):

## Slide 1

Simplified schematic for MOT coil control

CCM_0010 revC
Floating H-bridge
+ analog isolator

CCM_0008 revB
FET driver

CCM_0010 revC
Floating H-bridge
+ analog isolator

CCM_0008 revB
FET driver

Top h-bridge direction control (FP)

top

Top bypass control signal

Top bypass setpoint (FP)

Top bypass monitor (FP)

INTERLOCK(S)

bottom

Bottom bypass control signal

Bottom h-bridge direction control (FP)

Front panel

Q0 temp

12V
125A

Bottom bypass setpoint (FP)

external

Bottom bypass monitor (FP)

Q0

CCM_0008 revB
FET driver

0.01 ohms
100 W

Current control setpoint (FP)

Notes:
1. All 3 CCM_0008 FET drivers are lab ground referenced, which is possible by using galvanically isolated CASR current sensors
2. Anti-parallel FET pairs above h-bridge stages use the FET body diodes to provide (a) kickback protection and (b) biasing for bypass stages
3. Current can be monitored directly by measuring across the sense resistor at bottom of chain
4. CaF MOT coils + cabling are ~0.1 ohms (1V ~ 10A)
5. At 10A DC, Q0 dissipates ~80W (12V supply = 8V*10A)

Current monitor (FP)

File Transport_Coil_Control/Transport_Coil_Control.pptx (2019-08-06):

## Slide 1

Simplified schematic for transport coil control

CCM_0010 revC
Floating H-bridge
+ analog isolator

CCM_0008 revB
FET driver

CCM_0010 revC
Floating H-bridge
+ analog isolator

CCM_0008 revB
FET driver

Top h-bridge direction control (FP)

top

Top bypass control signal

Top bypass setpoint (FP)

Top bypass monitor (FP)

INTERLOCK(S)

Front panel

Q0 temp

External (fp)

Coil water
flow (rp)

FET water
flow

Q0

bottom

Bottom bypass control signal

Bottom h-bridge direction control (FP)

36V
276A

Bottom bypass setpoint (FP)

Bottom bypass monitor (FP)

Q1

CCM_0008 revB
FET driver

Current control setpoint (FP)

Notes:
1. All 3 CCM_0008 FET drivers are lab ground referenced, which is possible by using galvanically isolated CASR50 (bypass circuits) and LEM LF306-S current sensors
2. Anti-parallel FET pairs above h-bridge stages use the FET body diodes to provide (a) kickback protection and (b) biasing for bypass stages
3. Current can be monitored directly by measuring across the sense resistor at bottom of chain

Current monitor (FP)

0.01 ohms
100 W

LEM LF306-S

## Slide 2

5V

LED

5V

LED

12V-AUX

12V-AUX

10k

490

Interlock(s)

490

1k

2N3906

RC+

1k

2N3906

OTP1/2
FAN-FAIL1/2
DC-OK1/2
AC-FAIL1/2

GND-AUX

1k

10k

GND-AUX

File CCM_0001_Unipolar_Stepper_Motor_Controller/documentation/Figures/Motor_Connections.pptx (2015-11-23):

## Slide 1

Sanyo Denki 103H5210-0440 Stepper Motor
Unipolar hybrid 0.37 nm, 24V dc, 1.2A, 6 wires

2

Excitation Sequence

1 | 2 | 3 | 4 | 5 | 6
+ | + | 0 | + | 0 | +
+ | + | 0 | 0 | + | +
+ | 0 | + | 0 | + | +
+ | 0 | + | + | 0 | +

1

Output Sequence

A | B | C | D
0 | + | 0 | +
+ | 0 | 0 | +
+ | 0 | + | 0
0 | + | + | 0

Controller/Driver

+V

+V

A

C

B=!A

D=!C

CW

3

5

6

4

shield

A

B

C

D

+V

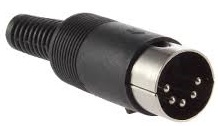
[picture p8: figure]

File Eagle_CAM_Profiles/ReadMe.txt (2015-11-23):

2layer.cam is a cam processor profile for generating gerber files from within Eagle (cadsoft).  At the moment of this writing it is quite generic and may produce gerber files that you don't need (such as a bottom stencil file).  You can alter the job profile and save it as a different configuration (for example, 2layer_simple.cam).  

How to use a cam profile:

Once your board is complete and has passed the design rules check, open the 'cam processor'.  Then file -> open job -> 2layer.cam (or equivalent).  When you process the job, the gerber files will be created.  File suffixes are summarized in another file in this directory.  I HIGHLY recommend that you inspect the files with a gerber file viewer before ordering your boards.  If something doesn't look quite right, or you've somehow left off component labels, etc., you can reconfigure the cam profile and rerun the job.  -NF.

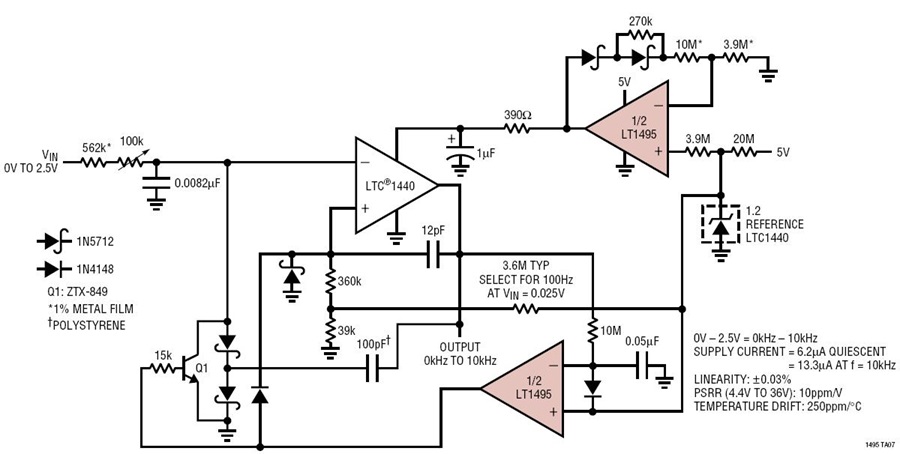
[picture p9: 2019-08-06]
CCM_0020_Floating_Leakage_Monitor/docs/FtoV_and_VtoF/13uA_0to10kHz_vtof_circuit.jpg

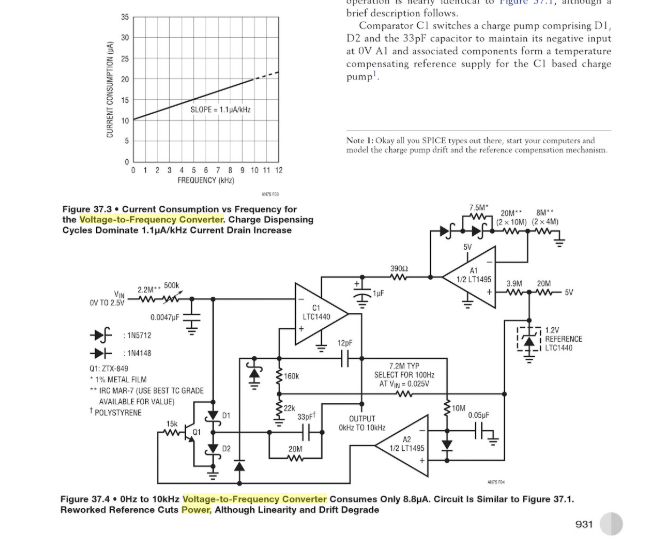
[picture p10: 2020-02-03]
CCM_0020_Floating_Leakage_Monitor/docs/FtoV_and_VtoF/Capture.PNG

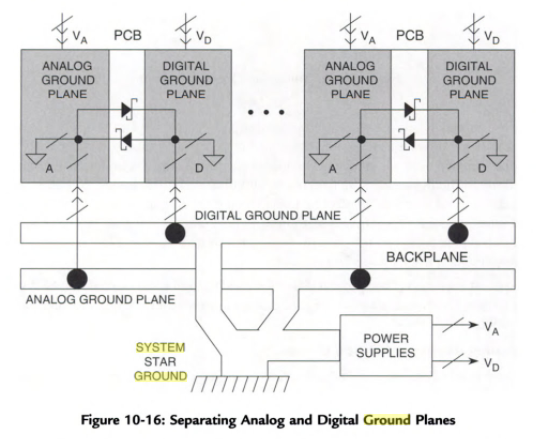
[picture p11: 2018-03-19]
CCM_0011_Subrack_Backplane/docs/Ground_Scheme.PNG

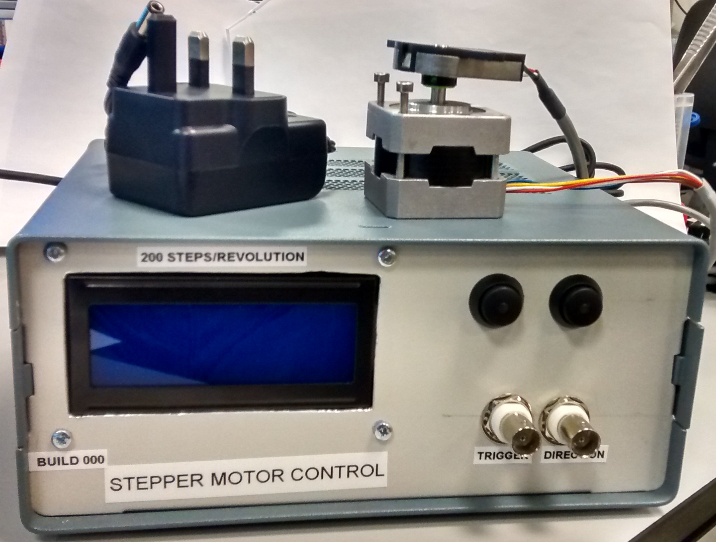
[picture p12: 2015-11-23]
CCM_0001_Unipolar_Stepper_Motor_Controller/documentation/Figures/Built_Box.jpg

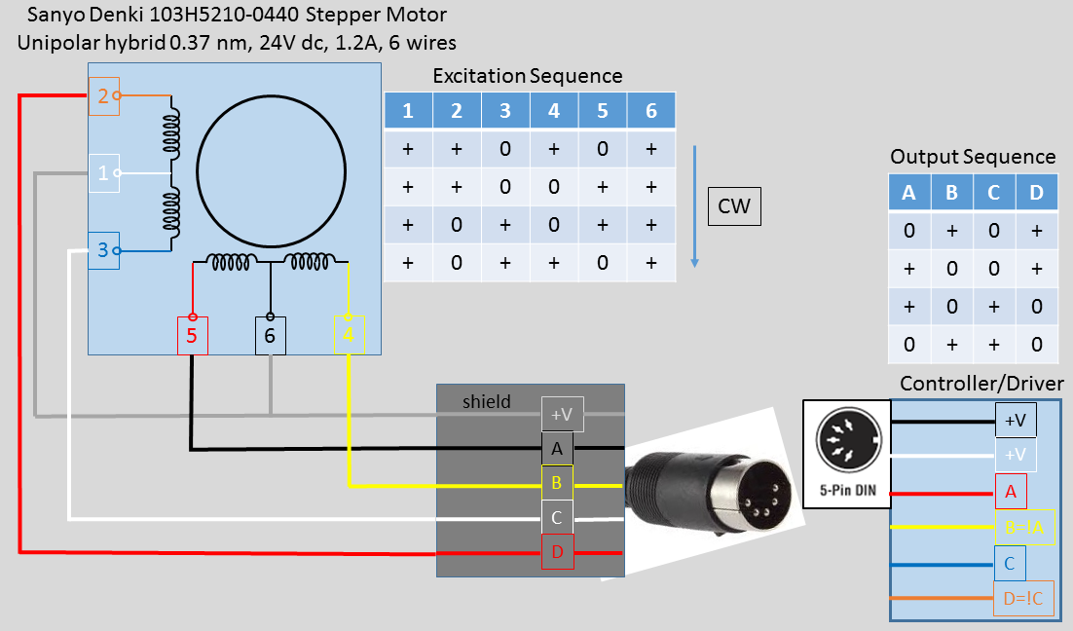
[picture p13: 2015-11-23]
CCM_0001_Unipolar_Stepper_Motor_Controller/documentation/Figures/Motor_Connections.png

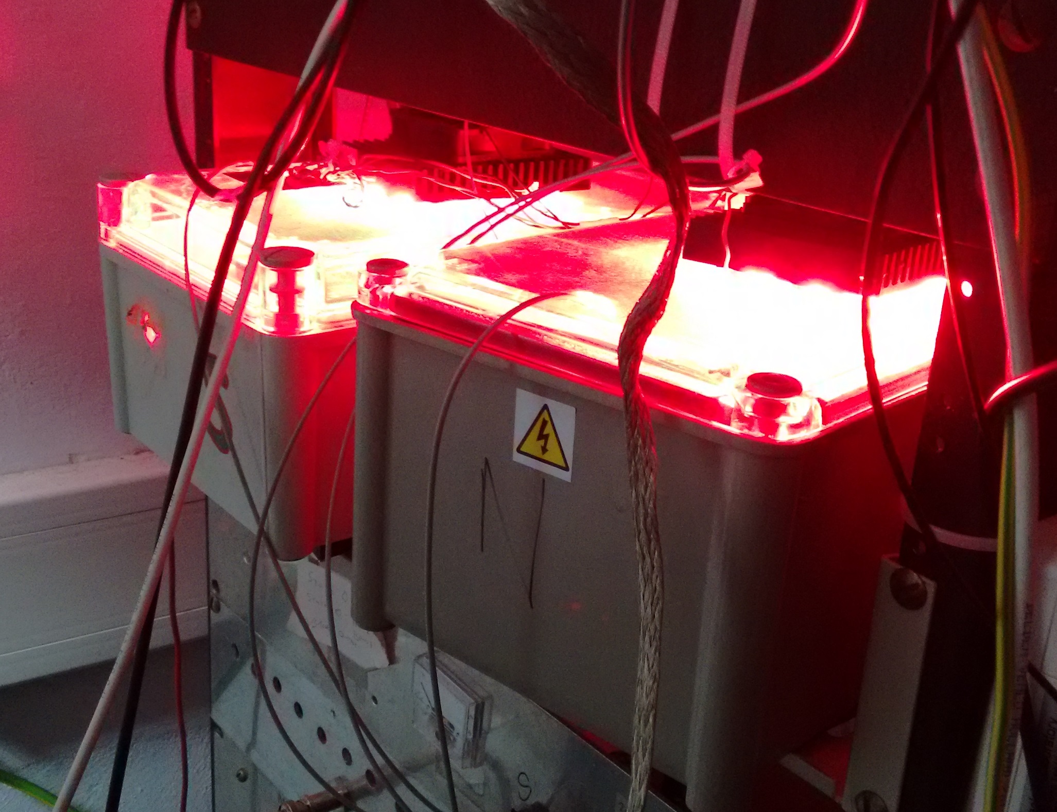
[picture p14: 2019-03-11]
LeakageMonitors/LeakOn.jpg

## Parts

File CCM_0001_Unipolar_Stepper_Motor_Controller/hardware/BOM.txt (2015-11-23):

Partlist exported from C:/Users/nfitch/Google Drive/Electronics/Projects/CCM_0001_Unipolar_Stepper_Motor_Controller/RevA/Circuit/Unipolar_Stepper_Motor_Controller_RevA.sch at 06/01/2015 10:42:07

Qty Value        Device              Package            Parts                                                                                                           Description                                           MF               MPN         OC_FARNELL OC_NEWARK
2                22-23-2061          22-23-2061         X2, X5                                                                                                          .100" (2.54mm) Center Header - 6 Pin                  MOLEX            22-23-2061  1462922    27C1933  
1                BILED               22-23-2021         LED7                                                                                                            DUO LED                                                                                                
1                CPOL-EUE5-13        E5-13              C14                                                                                                             POLARIZED CAPACITOR, European symbol                                                                   
1   0            RESISTOR0603-RES    0603-RES           R38                                                                                                             Resistor                                                                                               
1   0.1F         CPOL-USP128-60      P128-60            C30                                                                                                             POLARIZED CAPACITOR, American symbol                                                                   
23  0.1u         CAP0603-CAP         0603-CAP           C2, C9, C13, C16, C17, C18, C19, C20, C21, C23, C25, C26, C27, C28, C29, C31, C32, C33, C34, C35, C36, C37, C38 Capacitor                                                                                              
2   0.5          R-US_R2512          R2512              R11, R24                                                                                                        RESISTOR, American symbol                                                                              
2   1-227161-0   1-227161-0          AMP_227161         X3, X4                                                                                                          JACK,  RIGHT ANGLE, 50 OHM, PCB, BNC                  TYCO ELECTRONICS 1-227161    unknown    33B3200  
6   100          RESISTOR0603-RES    0603-RES           R3, R16, R20, R23, R33, R40                                                                                     Resistor                                                                                               
8   10k          RESISTOR0603-RES    0603-RES           R13, R22, R25, R26, R29, R30, R32, R39                                                                          Resistor                                                                                               
4   10u          CAP_POL1206         EIA3216            C7, C10, C11, C24                                                                                               Capacitor Polarized                                                                                    
7   1k           RESISTOR0603-RES    0603-RES           R6, R7, R14, R15, R19, R35, R41                                                                                 Resistor                                                                                               
3   1nF          CAP0603-CAP         0603-CAP           C3, C8, C12                                                                                                     Capacitor                                                                                              
1   20MHz        CRYSTALTC26V        TC26V              Q1                                                                                                              CRYSTAL                                                                                                
1   22-23-2021   22-23-2021          22-23-2021         X6                                                                                                              .100" (2.54mm) Center Header - 2 Pin                  MOLEX            22-23-2021  1462926    25C3832  
2   22-23-2031   22-23-2031          22-23-2031         X8, X10                                                                                                         .100" (2.54mm) Center Header - 3 Pin                  MOLEX            22-23-2031  1462950    30C0862  
1   22-23-2041   22-23-2041          22-23-2041         X12                                                                                                             .100" (2.54mm) Center Header - 4 Pin                  MOLEX            22-23-2041  1462920    38C0355  
2   22-23-2051   22-23-2051          22-23-2051         X1, X7                                                                                                          .100" (2.54mm) Center Header - 5 Pin                  MOLEX            22-23-2051  1462952    38C9178  
1   22k          RESISTOR0603-RES    0603-RES           R12                                                                                                             Resistor                                                                                               
2   22p          CAP0603-CAP         0603-CAP           C15, C22                                                                                                        Capacitor                                                                                              
1   24AA1025     24AA16SN            SO-08              IC4                                                                                                             Serial EEPROM                                         MICROCHIP        24AA16-I/SN 1331289    96K4056  
2   27           RESISTOR0603-RES    0603-RES           R8, R9                                                                                                          Resistor                                                                                               
1   3.3nF        CAP0603-CAP         0603-CAP           C1                                                                                                              Capacitor                                                                                              
2   300          RESISTOR0603-RES    0603-RES           R34, R36                                                                                                        Resistor                                                                                               
1   30k          RESISTOR0603-RES    0603-RES           R18                                                                                                             Resistor                                                                                               
3   4.7k         RESISTOR0603-RES    0603-RES           R10, R27, R31                                                                                                   Resistor                                                                                               
1   4148         DIODESOT23          SOT23-3            D1                                                                                                              Diode                                                                                                  
1   470uF        CPOL-EUSANYO_SMD_F8 SANYO-OSCON_SMD_F8 C4                                                                                                              POLARIZED CAPACITOR, European symbol                                                                   
2   47p          CAP0603-CAP         0603-CAP           C5, C6                                                                                                          Capacitor                                                                                              
2   50           R-US_R2512          R2512              R4, R5                                                                                                          RESISTOR, American symbol                                                                              
1   500k         RESISTOR0603-RES    0603-RES           R44                                                                                                             Resistor                                                                                               
6   5k           RESISTOR0603-RES    0603-RES           R1, R2, R17, R21, R28, R45                                                                                      Resistor                                                                                               
7   74AHC1G08DBV 74AHC1G08DBV        SOT23-5            IC2, IC7, IC8, IC9, IC11, IC13, IC19                                                                            2-input AND gate                                                                                       
1   74HC1G04     74AHC1G04DBV        SOT23-5            IC12                                                                                                            INVERTER Gate                                                                                          
2   74HC1G08     74AHC1G08DBV        SOT23-5            IC22, IC23                                                                                                      2-input AND gate                                                                                       
2   74HC1G125    74AHC1G125DBV       SOT23-5            IC10, IC16                                                                                                      Single Bus Buffer Gate with 3-State Output                                                             
2   74HC1G126    74AHC1G126DBV       SOT23-5            IC15, IC17                                                                                                      Single Bus Buffer Gate With 3-State Outputs                                                            
1   7805         7824DT              TO252              IC1                                                                                                             Positive VOLTAGE REGULATOR                                                                             
4   BZX84        ZENER-DIODESOT23    SOT23              D12, D16, D18, D20                                                                                              Z-Diode                                                                                                
1   DS3231M      DS3231M             8-SOIC             IC6                                                                                                             RTC (real time clock), I2C communication                                                               
1   FT230XS      FT230XS             SSOP16             IC3                                                                                                             USB to BASIC UART IC                                                                                   
1   HCTL-2021    HCTL-2021           PLCC20             IC14                                                                                                            HCTL-2021 Quadrature decoder from Avago Technologies.                                                  
4   IRLL024      NMOSSOT223          SOT223             T1, T2, T3, T4                                                                                                  MOS FET                                                                            unknown    unknown  
1   L297SM       L297SM              SO20               IC5                                                                                                             STEPPER MOTOR CONTROLLER                                                                               
1   LTC6993-1    LTC6993-1           SOT23-6            IC25                                                                                                                                                                                                                   
1   PIC18F46K80  PIC18F46K80         TQFP44_MC          IC18                                                                                                                                                                                                                   
8   RS2G-E3/52T  DIODE-DO214AA       DO214AA            D10, D11, D13, D14, D15, D17, D19, D21                                                                          DIODE                                                                                                  
3   TESTPOINT    TESTPOINT           TESTPOINT          TP1, TP2, TP3                                                                                                                                                                                                          
1   dni          RESISTOR0603-RES    0603-RES           R37                                                                                                             Resistor                                                                                               
8   red          LEDCHIPLED_0603     CHIPLED_0603       LED1, LED2, LED3, LED4, LED5, LED6, LED8, LED10                                                                 LED

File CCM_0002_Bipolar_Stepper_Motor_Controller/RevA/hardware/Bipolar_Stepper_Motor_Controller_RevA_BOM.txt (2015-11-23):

Partlist exported from C:/Users/nfitch/Google Drive/Electronics/Projects/CCM_0002_Bipolar_Stepper_Motor_Controller/RevA/Circuit/Bipolar_Stepper_Motor_Controller_RevA.sch at 10/11/2014 11:08:58

Qty Value        Device              Package            Parts                                     Description                                           
1   0.1F         CPOL-USP128-60      P128-60            C30                                       POLARIZED CAPACITOR, American symbol                  
9   0.1u         CAP0603-CAP         0603-CAP           C2, C9, C13, C16, C18, C19, C25, C26, C27 Capacitor                                             
2   0.5          R-US_R2512          R2512              R14, R15                                  RESISTOR, American symbol                             
2   1-227161-0   1-227161-0          AMP_227161         X3, X4                                    JACK,  RIGHT ANGLE, 50 OHM, PCB, BNC                  
3   10k          RESISTOR            0805               R13, R22, R32                             Resistor                                              
5   10k          RESISTOR0603-RES    0603-RES           R25, R26, R29, R30, R39                   Resistor                                              
4   10u          CAP_POL1206         EIA3216            C7, C10, C11, C24                         Capacitor Polarized                                   
8   1k           RESISTOR            0805               R6, R7, R33, R35, R37, R38, R41, R43      Resistor                                              
1   1k           RESISTOR0603-RES    0603-RES           R19                                       Resistor                                              
3   1nF          CAP0603-CAP         0603-CAP           C3, C8, C12                               Capacitor                                             
4   2-56         2-56                2-56               U$1, U$2, U$3, U$4                                                                              
4   22-23-2031   22-23-2031          22-23-2031         X6, X8, X10, X11                          .100" (2.54mm) Center Header - 3 Pin                  
2   22-23-2041   22-23-2041          22-23-2041         X5, X12                                   .100" (2.54mm) Center Header - 4 Pin                  
2   22-23-2051   22-23-2051          22-23-2051         X1, X7                                    .100" (2.54mm) Center Header - 5 Pin                  
1   22k          RESISTOR0603-RES    0603-RES           R12                                       Resistor                                              
2   27           RESISTOR            0805               R8, R9                                    Resistor                                              
1   3.3nF        CAP0603-CAP         0603-CAP           C1                                        Capacitor                                             
4   300          RESISTOR            0805               R34, R36, R40, R42                        Resistor                                              
1   30k          RESISTOR0603-RES    0603-RES           R18                                       Resistor                                              
1   4.7k         RESISTOR            0805               R10                                       Resistor                                              
2   4.7k         RESISTOR0603-RES    0603-RES           R27, R31                                  Resistor                                              
1   4148         DIODESOT23          SOT23-3            D1                                        Diode                                                 
1   470uF        CPOL-EUSANYO_SMD_F8 SANYO-OSCON_SMD_F8 C4                                        POLARIZED CAPACITOR, European symbol                  
2   47p          CAP0805             0805               C5, C6                                    Capacitor                                             
2   50           R-US_R2512          R2512              R4, R5                                    RESISTOR, American symbol                             
3   5k           RESISTOR0603-RES    0603-RES           R28, R44, R45                             Resistor                                              
3   74AHC1G08DBV 74AHC1G08DBV        SOT23-5            IC4, IC11, IC13                           2-input AND gate                                      
1   7805         7824DT              TO252              IC1                                       Positive VOLTAGE REGULATOR                            
1   DS3231M      DS3231M             8-SOIC             IC6                                       RTC (real time clock), I2C communication              
1   FT230XS      FT230XS             SSOP16             IC3                                       USB to BASIC UART IC                                  
1   HCTL-2021    HCTL-2021           PLCC20             IC14                                      HCTL-2021 Quadrature decoder from Avago Technologies. 
1   L297SM       L297SM              SO20               IC5                                       STEPPER MOTOR CONTROLLER                              
1   L298         L298                MULTIWATT-15       IC10                                      DUAL FULL-BRIDGE DRIVER                               
1   MX045-4MHz   SG531               DIL08-4            OSC1                                      CRYSTAL RESONATOR                                     
1   PIC18F46K80  PIC18F46K80         TQFP44_MC          IC12                                                                                            
1   RJ11-6PTH    RJ11-6PTH           RJ11-6             J1                                        RJ11 Jack                                             
8   RS2G-E3/52T  DIODE-DO214AA       DO214AA            D2, D3, D4, D5, D6, D7, D8, D9            DIODE                                                 
1   SL_70543_2   SL_70543_2          SL_70543_2         X31                                                                                             
3   red          LEDCHIPLED_0603     CHIPLED_0603       LED6, LED7, LED8                          LED                                                   
2   red          LEDCHIPLED_0805     CHIPLED_0805       LED1, LED10                               LED

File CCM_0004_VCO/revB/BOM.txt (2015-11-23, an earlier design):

Partlist exported from C:/Users/nfitch/Google Drive/Imperial/Electronics/CCM_0004_VCO/revB/CCM0004.sch at 07/05/2015 15:25:44

Qty Value      Device          Package      Parts                        Description                                                MF    MPN        OC_FARNELL OC_NEWARK
6   0.1        CAPACITOR0603   0603         C1, C2, C3, C7, C8, C11                                                                                                      
4   0.1        CAPACITOR2010   2010         C4, C5, C17, C18                                                                                                             
1   1000pF     CAPACITOR2010   2010         C10                                                                                                                          
1   100pF      CAPACITOR0603   0603         C9                                                                                                                           
7   10k        RESISTOR0603    0603         R1, R2, R3, R4, R5, R11, R12 RESISTOR, American symbol                                                                       
1   10k        RESISTOR2010    2010         R10                          RESISTOR, American symbol                                                                       
1   180        RESISTOR2010    2010         R9                           RESISTOR, American symbol                                                                       
1   22-23-2031 22-23-2031      22-23-2031   X4                           .100" (2.54mm) Center Header - 3 Pin                       MOLEX 22-23-2031 1462950    30C0862  
1   22-23-2041 22-23-2041      22-23-2041   X3                           .100" (2.54mm) Center Header - 4 Pin                       MOLEX 22-23-2041 1462920    38C0355  
1   270        RESISTOR2010    2010         R8                           RESISTOR, American symbol                                                                       
1   50         RESISTOR2010    2010         R7                           RESISTOR, American symbol                                                                       
1   530        RESISTOR2010    2010         R6                           RESISTOR, American symbol                                                                       
1   7812DT     7812DT          TO252        IC1                          Positive VOLTAGE REGULATOR                                                                      
1   BU-SMA-V   BU-SMA-V        BU-SMA-V     X1                           FEMALE SMA CONNECTOR                                                                            
1   CA3140D    CA3140D         SO08         IC2                          OP AMP                                                                                          
1   CA3140_BD  CA3140_BD       SO08         IC8                          OP AMP                                                                                          
1   LAT        LAT             MMM168       IC4                          Minicircuits surface mount attenuator                                                           
1   MAB32      MAB32           MAB32        X2                           CONNECTOR                                                                                       
1   MAR3       MAR3            MAR          IC5                          MiniCircuits MAR-3+ amplifier                                                                   
1   MAV11      MAV11           MAR          IC7                          MiniCircuits MAV-11 amplifer, currently identical to MAR-3                                      
1   MMBT3906   MMBT3906LT1SMD  SOT23-BEC    T2                           PNP Transistror                                                                                 
1   POS-50+    POS             A01          IC3                          MiniCircuits POS-x VCO, through hole package                                                    
1   SYAS-1     SYAS-1          TTT166       IC6                          MiniCircuits voltage variable attenuator                                                        
2   TCCH-80    TCCH-80         PL-147       L1, L2                       MiniCircuits TCCH-80+ choke                                                                     
2   TESTPOINT  TESTPOINT       TESTPOINT    TP1, TP2                                                                                                                     
1   red        LEDCHIPLED_0603 CHIPLED_0603 LED1                         LED

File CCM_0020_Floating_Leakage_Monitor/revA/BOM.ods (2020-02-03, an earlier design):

 | Transmitter Side Parts
 | Part type | Value | Quantity | Package | Schematic No | Part number | Notes | Total no for both boards | Product Page
have | Resistor | 0 | 1 | 0603 | R18 |  | Hysteresis placeholder | 1
x | Resistor | 10M | 2 | 0603 | R9, R16 |  |  | 2
have | Resistor | 10k | 1 | 0603 | R2 |  |  | 6
x | Resistor | 15k | 1 | 0603 | R6 |  |  | 1
have | Resistor | 1G | 1 | 2512 | R1 |  | Sense resistor | 1
have | Resistor | 1k | 2 | 0603 | R3, R14 |  |  | 7
x | Resistor | 270k | 1 | 0603 | R10 |  |  | 1
3.3M | Resistor | 3.6M | 1 | 0603 | R15 |  |  | 1
x | Resistor | 3.9M | 2 | 0603 | R5, R8 |  |  | 2
x | Resistor | 360k | 1 | 0603 | R12 |  |  | 1
x | Resistor | 39k | 1 | 0603 | R13, R17 |  |  | 1
x | Resistor | 4.3k | 1 | 0603 | R20 |  |  | 1
x | Resistor | 562k | 1 | 0603 | R4 |  | 1% metal film | 1
x | Trimpot | 100k | 1 |  | R7 | 3386C-1-104 |  | 5 | https://www.mouser.co.uk/ProductDetail/Bourns/3386C-1-104LF?qs=sGAEpiMZZMvygUB3GLcD7rufck0TIBKyw2qdK8hIS4E%3D
x | Capacitor | 50n | 1 | 0603 | C5 |  |  | 1
have | Capacitor | 0.1u | 6 | 0603 | C6, C8, C10, C11, C12, C17 |  |  | 24
have | Capacitor | 100p | 1 | 0603 | C3 |  | Styrene | 1
x | Capacitor | 12p | 1 | 0603 | C2 |  |  | 1
have | Capacitor | 4.7u | 2 | 0603 | C7, C15 |  |  | 5
x | Capacitor | 8.2n | 1 | 0603 | C1 |  |  | 1
have | Capacitor | 1u | 1 | 0603 | C4 |  |  | 2
x | Diode | 1N4148 | 2 | SOD-323 | D8, D11 | 1N4148 |  | 5 | https://www.mouser.co.uk/ProductDetail/Micro-Commercial-Components-MCC/1N4148WX-TP
x | Schottky | BAS70 | 9 | SOT23 | D1-D7, D9, D10 | BAS70 |  | 11 | https://www.mouser.co.uk/ProductDetail/Diodes-Incorporated/BAS70-7-F
x | MOSFET | BSS84 | 1 | SOT23 | Q5 | BSS84 |  | 1 | https://www.mouser.co.uk/ProductDetail/ON-Semiconductor-Fairchild/BSS84
x | JFET | SMP4117 | 4 | SOT23 | Q1, Q2, Q3, Q4 | SMP4117 |  | 4 | https://www.mouser.co.uk/ProductDetail/InterFET/SMP4117
have | NPN BJT | 3904 | 1 | SOT23 | T1 | 3904 |  | 2 | https://www.mouser.co.uk/ProductDetail/Central-Semiconductor/CMPT3904G-TR
x | Op-amp | LMC6041 | 1 | SOIC-8 | IC1 | LMC6041 |  | 1 | https://www.mouser.co.uk/ProductDetail/Texas-Instruments/LMC6041IMX-NOPB
x | Op-amp | LT1494 | 1 | SO-8 | IC2 | LT1494 |  | 1 | https://www.mouser.co.uk/ProductDetail/Analog-Devices/LT1494CS8PBF
x | Dual op-amp | LT1495 | 1 | SO-8 | IC3 | LT1495 |  | 1 | https://www.mouser.co.uk/ProductDetail/Analog-Devices/LT1495CS8PBF
x | Comparator | LTC1440 | 1 | SO-8 | IC4 | LTC1440 |  | 1 | https://www.mouser.co.uk/ProductDetail/Analog-Devices/LTC1440CS8PBF
x | Voltage Regulator | LT6656 | 1 | SOT23-6 | IC6 | LT6656 |  | 1 | https://www.mouser.co.uk/ProductDetail/Analog-Devices/LT6656BCS6-5TRMPBF
have | Opto-isolator | OPI150 | 1 |  | LED1 | OPI150 |  | 1 | https://www.mouser.co.uk/ProductDetail/Optek-TT-Electronics/OPI150
 | NOT LISTED HERE
x | AAA Battery mounts
 | Current in connectors (marked on eagle as testpads)
x | Gas-discharge tube
 | Other resistor (R19 together with R18) to add hysteresis (2.4M and 100k are suggested values)
 | Receiver side Parts
 |  |  | 2
 | Part type | Value | Quantity | Package | Schematic No | Part number | Notes | Total no for both boards | Product Page
x | Resistor | 1.6k | 1 | 0603 | R15 |  |  | 1
have | Resistor | 100 | 1 | 0603 | R32 |  |  | 1
have | Resistor | 100k | 4 | 0603 | R22, R23, R28, R29 |  |  | 5
have | Resistor | 10k | 5 | 0603 | R6, R10, R30, R34, R36 |  |  | 6
x | Resistor | 180 | 1 | 0603 | R17 |  |  | 1
have | Resistor | 1M | 1 | 0603 | R8 |  |  | 1
have | Resistor | 1k | 5 | 0603 | R5, R11, R16, R18, R26 |  |  | 7
x | Resistor | 2.21k | 3 | 0603 | R12, R19, R23 |  |  | 3
x | Resistor | 2.87k | 1 | 0603 | R3 |  |  | 1
x | Resistor | 200k | 1 | 0603 | R33 |  |  | 1
x | Resistor | 22k | 1 | 0603 | R20 |  |  | 1
270 | Resistor | 274 | 1 | 0603 | R4 |  |  | 1
3.3M | Resistor | 3.48M | 1 | 0603 | R1 |  |  | 1
x | Resistor | 3.9k | 1 | 0603 | R14 |  |  | 1
422 | Resistor | 412 | 2 | 0603 | R24, R27 |  |  | 2
x | Resistor | 499 | 1 | 0603 | R2, R21 |  |  | 1
x | Resistor | 91k | 1 | 0603 | R31 |  |  | 1
have | Capacitor | 0.1u | 18 | 0603 | C3, C4, C5, C10, C12, C13, C14, C15, C16, C17, C18, C19, C20, C21, C22, C23, C25, C27 |  |  | 24
have | Capacitor | 10n | 1 | 0603 | C9 |  | NPO | 1
have | Capacitor | 1n | 1 | 0603 | C11 |  |  | 1
have | Capacitor | 1u | 1 | 0603 | C7 |  | Ideally polypropylene | 2
have | Capacitor | 3.3n | 1 | 0603 | C2 |  |  | 1
have | Capacitor | 4.7u | 3 | 0603 | C6, C24, C26 |  |  | 5
x | Capacitor | 750p | 1 | 0603 | C8 |  |  | 1
x | LED | Red | 2 | 0603 | LED1, LED2 | SML-D12V8W |  | 2 | https://www.mouser.co.uk/ProductDetail/ROHM-Semiconductor/SML-D12V8WT86C
x | Diode | 1N4148 | 3 | SOD-323 | D2, D3, D4 | 1N4148 |  | 5 | https://www.mouser.co.uk/ProductDetail/Bourns/3386C-1-104LF?qs=sGAEpiMZZMvygUB3GLcD7rufck0TIBKyw2qdK8hIS4E%3D
have | 2-pin Molex | 22-23-2021 | 2 |  | X1, X2 | 22-23-2021 |  | 2 | https://www.mouser.co.uk/ProductDetail/Molex/22-23-2021
have | 3-pin Molex | 22-23-2031 | 1 |  | X3 | 22-23-2031 | (+15V, -15V, GND) | 1 | https://www.mouser.co.uk/ProductDetail/Molex/22-23-2031
x | Trimpot | 250-Variable | 1 |  | R25 | M64Y201KB40 |  | 1 | https://www.mouser.co.uk/ProductDetail/Vishay-Spectrol/M64Y201KB40
x | Trimpot | 2k-Variable | 1 |  | R35 | M64Y202KB40 |  | 1 | https://www.mouser.co.uk/ProductDetail/Vishay-Spectrol/M64Y202KB40
have | NPN BJT | 3904 | 1 | SOT23 | T1 | 3904 |  | 2 | https://www.mouser.co.uk/ProductDetail/Central-Semiconductor/CMPT3904G-TR
have | PNP BJT | 3906 | 1 | SOT23 | T2 | 3906 |  | 1 | https://www.mouser.co.uk/ProductDetail/Central-Semiconductor/CMPT3906G-TR
x | NAND Gate | 74AHC1G00DBV | 1 | SOT23-5 | IC4 | 74AHC1G00DBV |  | 1 | https://www.mouser.co.uk/ProductDetail/Texas-Instruments/SN74AHC1G00DBVR
x | NOT gate | 74AHC1G04DBV | 3 | SOT23-5 | IC5, IC6, IC7 | 74AHC1G04DBV |  | 3 | https://www.mouser.co.uk/ProductDetail/Texas-Instruments/SN74AHC1G04DBVR
x | D Flip-flop | 74LCV2G74 | 2 | TSSOP8 | U1, U2 | 74LCV2G74 |  | 2 | https://www.mouser.co.uk/ProductDetail/Nexperia/74LVC2G74DP125?qs=me8TqzrmIYX1iMHaYTXJug%3D%3D
x | Voltage Regulator | 7805 | 1 | TO252 | IC3 | 7805 |  | 1 | https://www.mouser.co.uk/ProductDetail/ON-Semiconductor/MC7805BDTRKG
x | V to F | AD654 | 1 | SOIC-8 | IC9 | AD654 |  | 1 | https://www.mouser.co.uk/ProductDetail/Analog-Devices/AD654JRZ
have | Op-amp | AD820 | 1 | SOIC-8 | IC8 | AD820 |  | 1 | https://www.mouser.co.uk/ProductDetail/Analog-Devices/AD820ARZ
x | Op-amp | AD8656 | 1 | SOIC-8 | IC1 | AD8656 |  | 1 | https://www.mouser.co.uk/ProductDetail/Analog-Devices/AD8656ARZ
have | Op-amp | LF356 | 2 | SOIC-8 | IC10, IC11 | LF356 |  | 2 | https://www.mouser.co.uk/ProductDetail/Texas-Instruments/LF356MX-NOPB
x | Comparator | LM311D | 1 | SOIC-8 | IC2 | LM311D |  | 1 | https://www.mouser.co.uk/ProductDetail/Texas-Instruments/LM311D
x | NPN darlington | MMBTA13LT1 | 1 | SOT23 | Q1 | MMBTA13LT1 |  | 1 | https://www.mouser.co.uk/ProductDetail/ON-Semiconductor/MMBTA13LT1G
x | Zener Diode | 1.25V | 1 | SOT23 | D1 | MAX6006 |  | 1 | https://www.mouser.co.uk/ProductDetail/Maxim-Integrated/MAX6006AEUR%2bT
x | Zener Diode | 2.5V | 1 | SOT23 | D7 | LM4040 |  | 1 | https://www.mouser.co.uk/ProductDetail/Diodes-Incorporated/LM4040C25QFTA
x | Schottky | BAS70 | 2 | SOT23 | D5, D6 | BAS70 |  | 11 | https://www.mouser.co.uk/ProductDetail/Diodes-Incorporated/BAS70-7-F
 | NOT LISTED HERE
 | C1, the transimpedance feedback capacitor marked DNI

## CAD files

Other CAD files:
CCM_0008_Precision_FET_Driver/revA/controller/cad/002.ipt
CCM_0008_Precision_FET_Driver/revA/controller/cad/002001.ipt
CCM_0008_Precision_FET_Driver/revA/controller/cad/002002.ipt
CCM_0008_Precision_FET_Driver/revA/controller/cad/002003.ipt
CCM_0008_Precision_FET_Driver/revA/controller/cad/1.ipt
CCM_0008_Precision_FET_Driver/revA/controller/cad/1001.ipt
CCM_0008_Precision_FET_Driver/revA/controller/cad/1002.ipt
CCM_0008_Precision_FET_Driver/revA/controller/cad/1003.ipt
CCM_0008_Precision_FET_Driver/revA/controller/cad/3009P_ASM_Next_assembly_relationship;33256-61701.ipt
CCM_0008_Precision_FET_Driver/revA/controller/cad/3009P_ASM_Next_assembly_relationship;33256-61702.ipt
CCM_0008_Precision_FET_Driver/revA/controller/cad/3009P_ASM_Next_assembly_relationship;33256-61703.ipt
CCM_0008_Precision_FET_Driver/revA/controller/cad/3009P_ASM_Next_assembly_relationship;33256-61704.ipt
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

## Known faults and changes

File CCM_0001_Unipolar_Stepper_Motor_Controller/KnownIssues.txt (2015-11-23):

Known issues with RevA and planned changes for RevB:

-- HARDWARE:
-- Somehow I forgot a 10k pullup on the MCLR_ pin to 5V.  You'll need to add one manually in order for the PIC to run.
-- The USB connector is backwards with respect to the commercial cable, be careful you don't plug it in as is. 
-- For the next revision, it would be nice to control the Vref pin of the L297 driver from an analog output on the PIC (variable power).

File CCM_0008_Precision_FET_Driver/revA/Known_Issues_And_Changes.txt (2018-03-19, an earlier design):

Changes for Sid's experiment (all configured for unipolar):

1) swapped control signal differential inputs to give positive current for positive control voltage

2) removed input parallel RC on both control-signal inputs, replaced R31 with 0 ohms to local-ground reference the control signal (otherwise was floating beyond common-mode limits of input op-amps).

3) R5 -> 0 ohms seemed to improve tunability of feedback

4) current sensor is "inverted", JP4 is installed

5) current monitor circuit is just wrong but even after making it a buffer the output signal is inverted

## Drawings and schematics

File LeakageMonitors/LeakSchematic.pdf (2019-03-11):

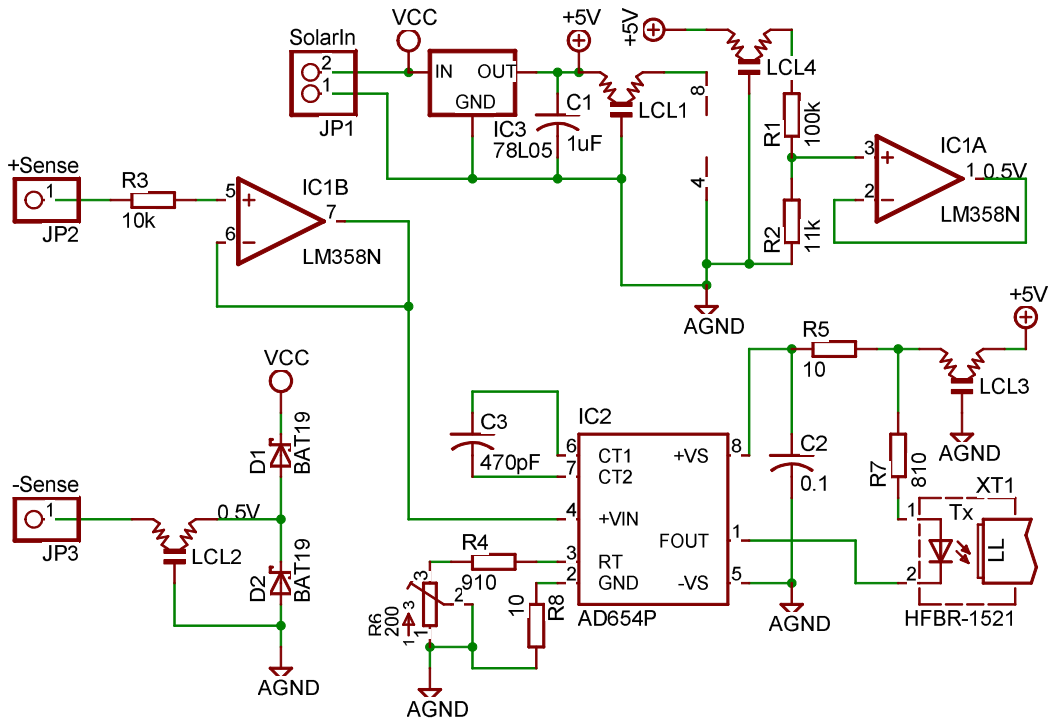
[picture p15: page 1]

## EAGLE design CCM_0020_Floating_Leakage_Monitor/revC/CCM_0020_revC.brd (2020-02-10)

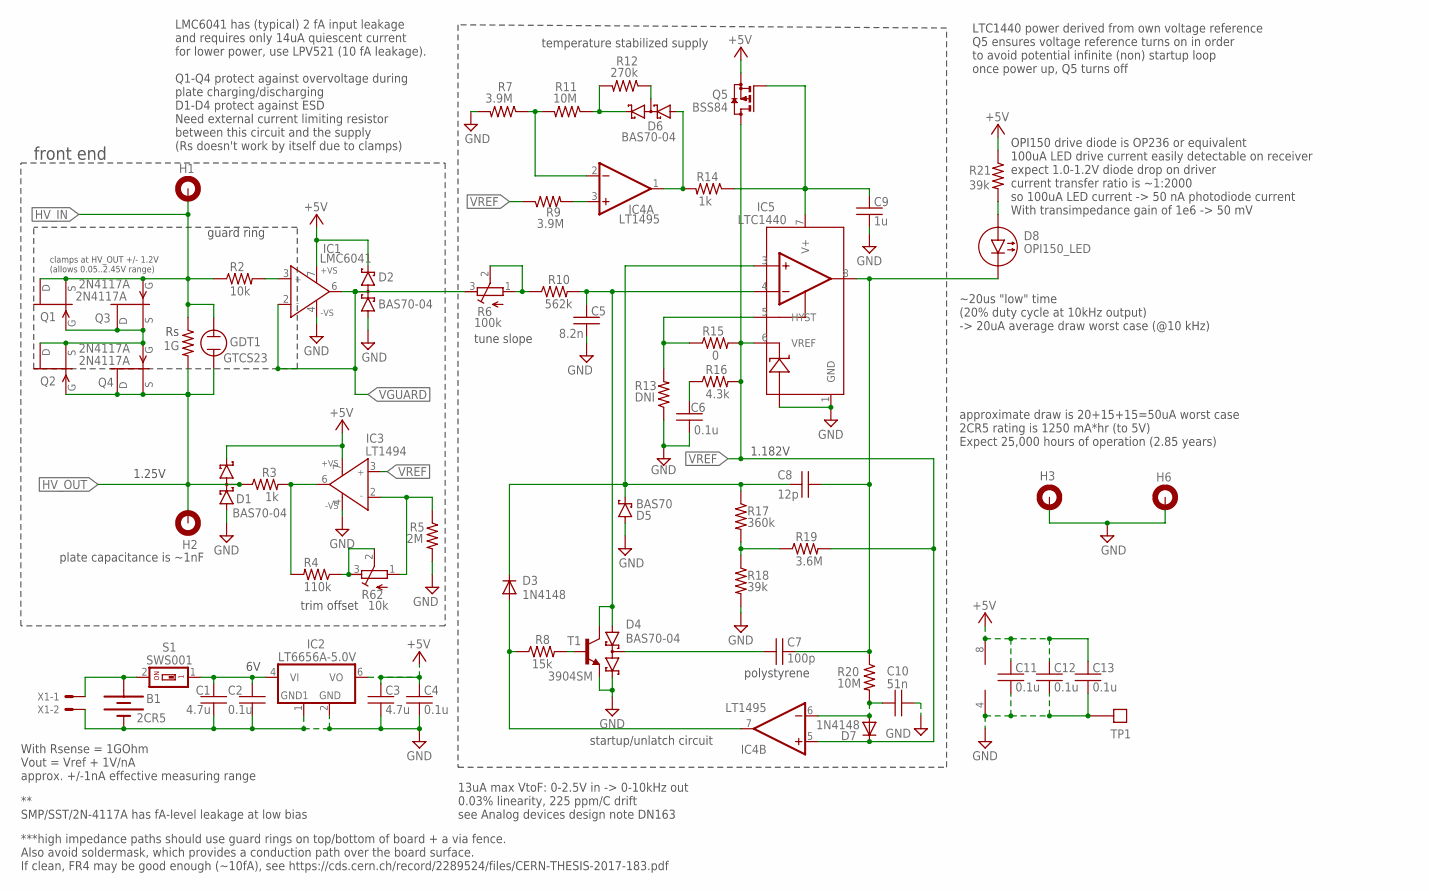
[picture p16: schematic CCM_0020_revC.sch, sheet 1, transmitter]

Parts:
B1: 2CR5
C1, C3: 4.7u; 0603
C2, C4, C6, C11, C12, C13: 0.1u; 0603
C5: 8.2n; 0603
C7: 100p; 0603
C8: 12p; 0603
C9: 1u; 0603
C10: 51n; 0603
D1, D2, D4, D6: BAS70-04; SOT23
D3, D7: 1N4148; SOD323_ST
D5: BAS70; SOD323_ST
D8: OPI150_LED
GDT1: GTCS23
H1, H2, H3, H6: MOUNT-PAD-ROUND3.0; 3,0-PAD
IC1: LMC6041; SO8
IC2: LT6656A-5.0V; SOT23-6
IC3: LT1494; SO8
IC4: LT1495; SO8
IC5: LTC1440; SO8
Q1, Q2, Q3, Q4: 2N4117A; SOT23
Q5: BSS84; SOT23
R1: 1G; 2512
R2: 10k; 0603
R3, R14: 1k; 0603
R4: 110k; 0603
R5: 2M; 0603
R6: 100k; RTRIM3224W
R7, R9: 3.9M; 0603
R8: 15k; 0603
R10: 562k; 0603
R11, R20: 10M; 0603
R12: 270k; 0603
R13: DNI; 0603
R15: 0; 0603
R16: 4.3k; 0603
R17: 360k; 0603
R18, R21: 39k; 0603
R19: 3.6M; 0603
R62: 10k; RTRIM3224W
S1: SWS001; SMS-001
T1: 3904SM; SOT23
TP1: TESTPOINT
X1: 22-23-2021

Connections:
+5V: C3.1, C4.1, C11.1, C12.1, C13.1, D1.2 (C2), D2.2 (C2), IC1.7 (+VS), IC2.6 (VO), IC3.7 (+VS), IC4.8 (V+), Q5.2 (S), R21.1
GND: B1.V- (-), C1.2, C2.2, C3.2, C4.2, C5.2, C6.1, C9.2, C10.2, C11.2, C12.2, C13.2, D1.1 (A1), D2.1 (A1), D4.2 (C2), D5.A, H3.B3,0, H6.B3,0, IC1.4 (-VS), IC2.1 (GND1), IC2.2 (GND), IC3.4 (-VS), IC4.4 (V-), IC5.1 (GND), IC5.2 (V-), R5.2, R7.2, R13.1, R18.2, T1.2 (E), TP1.P$1, X1.2
HV_IN: GDT1.P$1 (1), H1.B3,0, Q1.1 (D), Q1.2 (S), Q3.3 (G), R1.1, R2.1
HV_IN1: Q1.3 (G), Q2.1 (D), Q2.2 (S), Q3.1 (D), Q3.2 (S), Q4.3 (G)
HV_OUT: D1.3 (C1A2), GDT1.P$2 (2), H2.B3,0, Q2.3 (G), Q4.1 (D), Q4.2 (S), R1.2, R3.1
HYST: IC5.5 (HYST), R13.2, R15.1
unnamed: C9.1, IC5.7 (V+), Q5.1 (G), R14.1
unnamed: D8.P$1 (1(A)), R21.2
unnamed: R6.1 (A), R6.2 (S), R10.1
unnamed: IC1.3 (IN+), R2.2
unnamed: C6.2, R16.1
unnamed: C5.1, D4.1 (A1), IC5.4 (-IN), R10.2, T1.3 (C)
unnamed: C7.1, D4.3 (C1A2)
unnamed: R8.2, T1.1 (B)
unnamed: D3.A, IC4.7 (OUT), R8.1
unnamed: R17.2, R18.1, R19.1
unnamed: C8.1, D3.C, D5.C, IC5.3 (+IN), R17.1
unnamed: C10.1, D7.A, IC4.6 (-IN), R20.2
unnamed: D6.1 (A1), IC4.1 (OUT), R14.2
unnamed: D6.2 (C2), R11.1, R12.2
unnamed: IC4.2 (-IN), R7.1, R11.2
unnamed: C1.1, C2.1, IC2.4 (VI), S1.1
unnamed: D6.3 (C1A2), R12.1
unnamed: IC4.3 (+IN), R9.2
unnamed: IC3.2 (IN-), R5.1, R62.1 (A)
unnamed: IC3.6 (OUT), R3.2, R4.2
unnamed: R4.1, R62.2 (S), R62.3 (E)
unnamed: B1.V+ (+), S1.2, X1.1
VGUARD: D2.3 (C1A2), IC1.2 (IN-), IC1.6 (OUT), R6.3 (E)
VREF: D7.C, IC3.3 (IN+), IC4.5 (+IN), IC5.6 (VREF), Q5.3 (D), R9.1, R15.2, R16.2, R19.2
VTOF_OUTPUT: C7.2, C8.2, D8.P$2 (2(C)), IC5.8 (OUT), R20.1

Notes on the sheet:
** SMP/SST/2N-4117A has fA-level leakage at low bias
plate capacitance is ~1nF
With Rsense = 1GOhm Vout = Vref + 1V/nA approx. +/-1nA effective measuring range
***high impedance paths should use guard rings on top/bottom of board + a via fence. Also avoid soldermask, which provides a conduction path over the board surface. If clean, FR4 may be good enough (~10fA), see https://cds.cern.ch/record/2289524/files/CERN-THESIS-2017-183.pdf
polystyrene
front end
13uA max VtoF: 0-2.5V in -> 0-10kHz out 0.03% linearity, 225 ppm/C drift see Analog devices design note DN163
1.182V
clamps at HV_OUT +/- 1.2V (allows 0.05..2.45V range)
approximate draw is 20+15+15=50uA worst case 2CR5 rating is 1250 mA*hr (to 5V) Expect 25,000 hours of operation (2.85 years)
guard ring
~20us "low" time (20% duty cycle at 10kHz output) -> 20uA average draw worst case (@10 kHz)
OPI150 drive diode is OP236 or equivalent 100uA LED drive current easily detectable on receiver expect 1.0-1.2V diode drop on driver current transfer ratio is ~1:2000 so 100uA LED current -> 50 nA photodiode current With transimpedance gain of 1e6 -> 50 mV
LMC6041 has (typical) 2 fA input leakage and requires only 14uA quiescent current for lower power, use LPV521 (10 fA leakage). Q1-Q4 protect against overvoltage during plate charging/discharging D1-D4 protect against ESD Need external current limiting resistor between this circuit and the supply (R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
temperature stabilized supply
startup/unlatch circuit
tune slope
1.25V
LTC1440 power derived from own voltage reference Q5 ensures voltage reference turns on in order to avoid potential infinite (non) startup loop once power up, Q5 turns off
trim offset

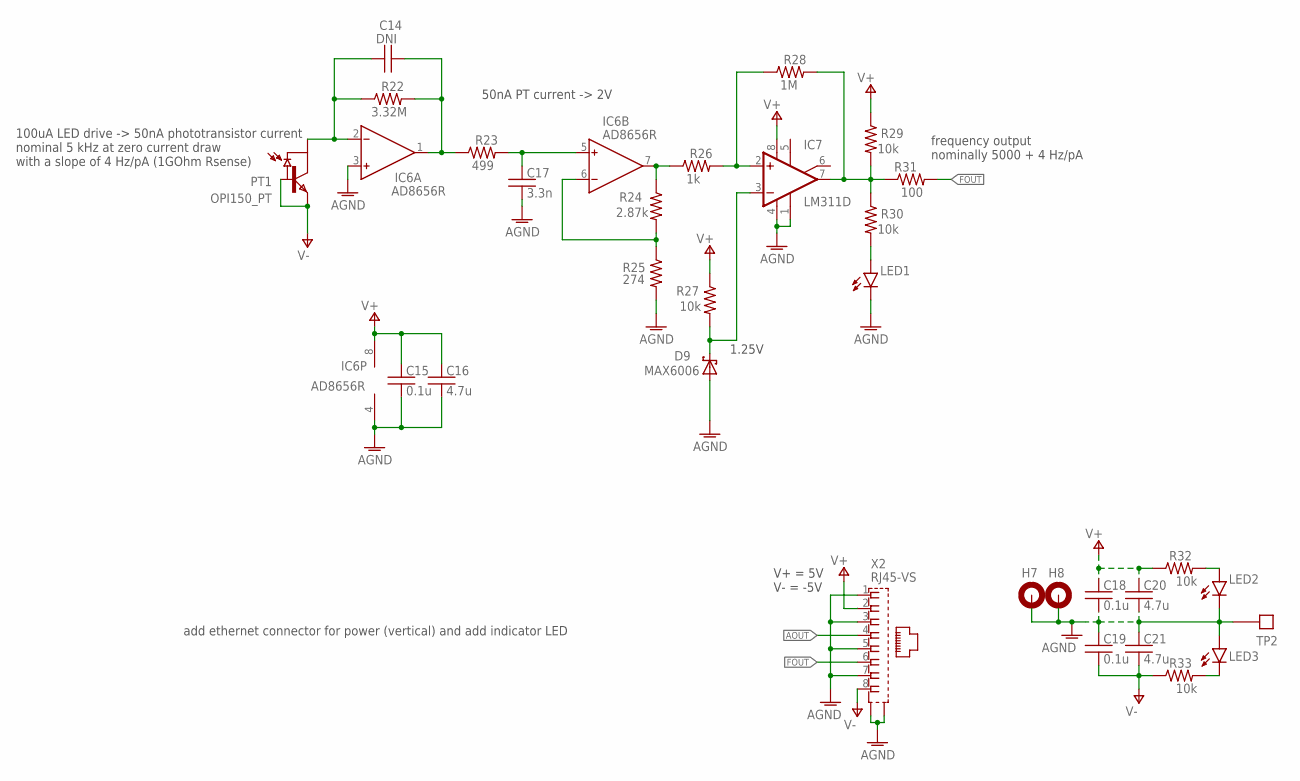
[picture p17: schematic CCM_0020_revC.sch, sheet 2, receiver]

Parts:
C14: DNI; 0603
C15, C18, C19: 0.1u; 0603
C16, C20, C21: 4.7u; 0603
C17: 3.3n; 0603
D9: MAX6006; SOT23
H7, H8: MOUNT-PAD-ROUND3.0; 3,0-PAD
IC6: AD8656R; SO8
IC7: LM311D; SO08
LED1, LED2, LED3: LEDCHIP-LED0603; CHIP-LED0603
PT1: OPI150_PT; OPI150_PHOTOTRANSISTOR
R22: 3.32M; 0603
R23: 499; 0603
R24: 2.87k; 0603
R25: 274; 0603
R26: 1k; 0603
R27, R29, R30, R32, R33: 10k; 0603
R28: 1M; 0603
R31: 100; 0603
TP2: TESTPOINT
X2: RJ45-VS

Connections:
AGND: C15.2, C16.2, C17.2, C18.2, C19.1, C20.2, C21.1, D9.2 (A), H7.B3,0, H8.B3,0, IC6.3 (IN+), IC6.4 (V-), IC7.1 (GND), IC7.4 (V-), LED1.C, LED2.C, LED3.A, R25.2, TP2.P$1, X2.1, X2.3, X2.5, X2.7, X2.S1, X2.S2; also elsewhere on the board
AOUT: X2.4; also elsewhere on the board
FOUT: R31.2, X2.6; also elsewhere on the board
unnamed: LED2.A, R32.2
unnamed: C14.1, IC6.2 (IN-), PT1.P3 (COLLECTOR), R22.1
unnamed: C14.2, IC6.1 (OUT), R22.2, R23.1
unnamed: C17.1, IC6.5 (IN+), R23.2
unnamed: IC6.6 (IN-), R24.2, R25.1
unnamed: IC6.7 (OUT), R24.1, R26.1
unnamed: IC7.2 (+IN), R26.2, R28.1
unnamed: D9.1 (C), IC7.3 (-IN), R27.2
unnamed: LED3.C, R33.2
unnamed: LED1.A, R30.2
unnamed: IC7.7 (OUT), R28.2, R29.2, R30.1, R31.1
V+: C15.1, C16.1, C18.1, C20.1, IC6.8 (V+), IC7.8 (V+), R27.1, R29.1, R32.1, X2.2; also elsewhere on the board
V-: C19.2, C21.2, PT1.P4 (BASE), PT1.P5 (EMITTER), R33.1, X2.8; also elsewhere on the board

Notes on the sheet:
100uA LED drive -> 50nA phototransistor current nominal 5 kHz at zero current draw with a slope of 4 Hz/pA (1GOhm Rsense)
50nA PT current -> 2V
1.25V
frequency output nominally 5000 + 4 Hz/pA
V+ = 5V V- = -5V
add ethernet connector for power (vertical) and add indicator LED

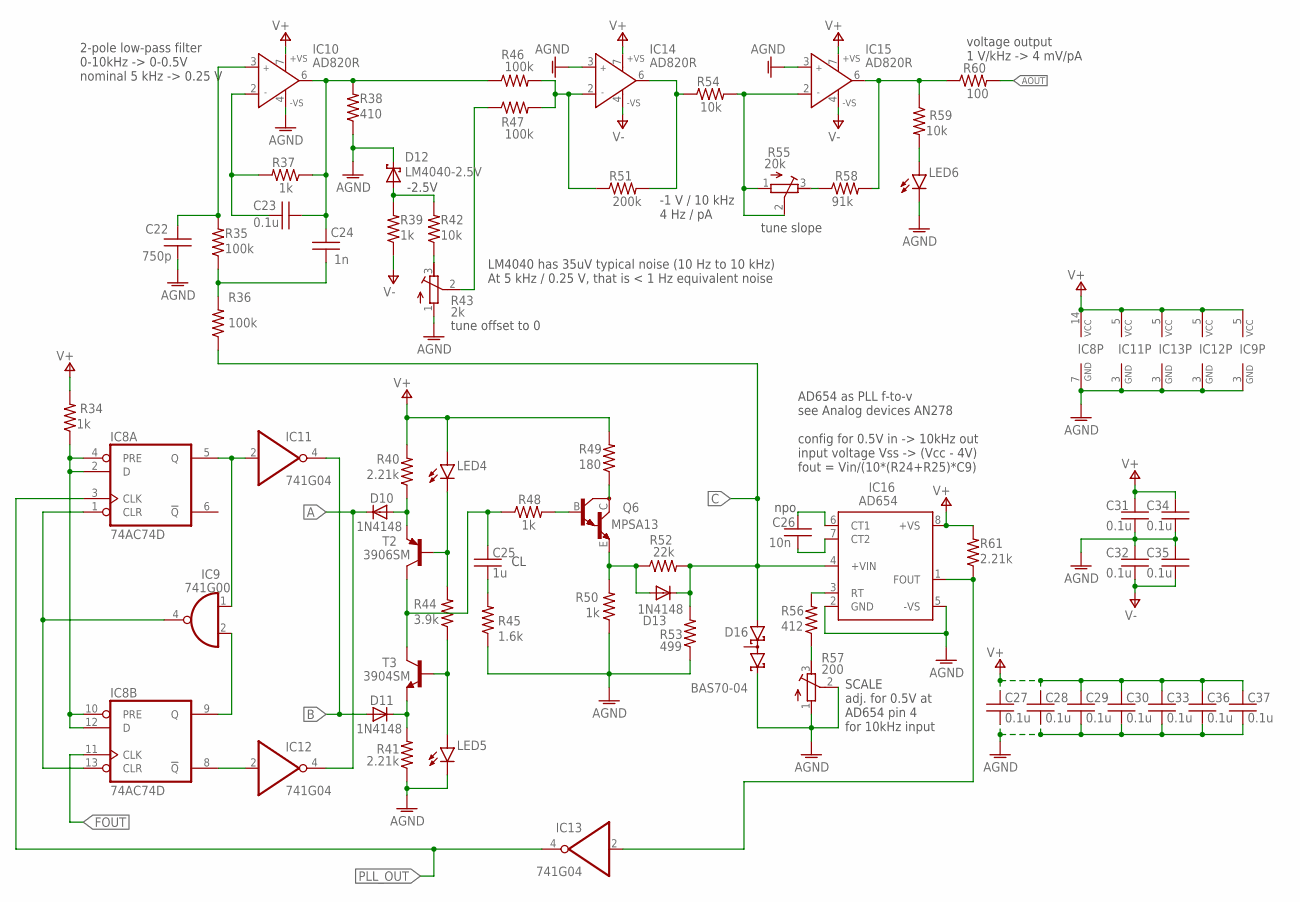
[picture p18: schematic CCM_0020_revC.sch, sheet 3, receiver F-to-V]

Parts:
C22: 750p; 0603
C23, C27, C28, C29, C30, C31, C32, C33, C34, C35, C36, C37: 0.1u; 0603
C24: 1n; 0603
C25: 1u; 0603
C26: 10n; 0603
D10, D11, D13: 1N4148; SOD323_ST
D12: LM4040-2.5V; SOT23
D16: BAS70-04; SOT23
IC8: 74AC74D; SO14
IC9: 741G00; SOT23-5
IC10, IC14, IC15: AD820R; SO8
IC11, IC12, IC13: 741G04; SOT23-5
IC16: AD654; SO08
LED4, LED5, LED6: LEDCHIP-LED0603; CHIP-LED0603
Q6: MPSA13; SOT23-BEC
R34, R37, R39, R48, R50: 1k; 0603
R35, R36, R46, R47: 100k; 0603
R38: 410; 0603
R40, R41, R61: 2.21k; 0603
R42, R54, R59: 10k; 0603
R43: 2k; RTRIM3224W
R44: 3.9k; 0603
R45: 1.6k; 0603
R49: 180; 0603
R51: 200k; 0603
R52: 22k; 0603
R53: 499; 0603
R55: 20k; RTRIM3224W
R56: 412; 0603
R57: 200; RTRIM3224W
R58: 91k; 0603
R60: 100; 0603
T2: 3906SM; SOT23-BEC
T3: 3904SM; SOT23

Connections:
A: D10.C, IC12.4 (O)
AGND: C22.1, C27.2, C28.2, C29.2, C30.2, C31.1, C32.2, C33.2, C34.1, C35.2, C36.2, C37.2, D12.1 (C), D16.2 (C2), IC8.7 (GND), IC9.3 (GND), IC10.4 (-VS), IC11.3 (GND), IC12.3 (GND), IC13.3 (GND), IC14.3 (IN+), IC15.3 (IN+), IC16.2 (GND), IC16.5 (-VS), LED5.C, LED6.C, R38.1, R41.1, R43.1 (A), R45.1, R50.1, R53.1, R57.1 (A), R57.2 (S); also elsewhere on the board
AOUT: R60.2; also elsewhere on the board
B: D11.A, IC11.4 (O)
C: D13.C, D16.1 (A1), IC16.4 (+VIN), R36.1, R52.2, R53.2
FOUT: IC8.11 (CLK); also elsewhere on the board
unnamed: IC8.1 (CLR), IC8.13 (CLR), IC9.4 (O)
unnamed: IC8.9 (Q), IC9.2 (I1)
unnamed: IC8.8 (!Q), IC12.2 (I)
unnamed: IC8.5 (Q), IC9.1 (I0), IC11.2 (I)
unnamed: R56.1, R57.3 (E)
unnamed: C25.1, R48.1, T2.C, T3.3 (C)
unnamed: D11.C, R41.2, T3.2 (E)
unnamed: LED4.C, R44.2, T2.B
unnamed: LED5.A, R44.1, T3.1 (B)
unnamed: C25.2, R45.2
unnamed: Q6.C, R49.1
unnamed: Q6.B, R48.2
unnamed: D13.A, Q6.E, R50.2, R52.1
unnamed: IC16.3 (RT), R56.2
unnamed: C26.1, IC16.6 (CT1)
unnamed: C26.2, IC16.7 (CT2)
unnamed: IC13.2 (I), IC16.1 (FOUT), R61.1
unnamed: C24.1, R35.1, R36.2
unnamed: C22.2, IC10.3 (IN+), R35.2
unnamed: C23.2, C24.2, IC10.6 (OUT), R37.1, R38.2, R46.1
unnamed: C23.1, IC10.2 (IN-), R37.2
unnamed: IC14.2 (IN-), R46.2, R47.2, R51.1
unnamed: IC15.2 (IN-), R54.2, R55.1 (A), R55.2 (S)
unnamed: IC15.6 (OUT), R58.2, R59.1, R60.1
unnamed: IC14.6 (OUT), R51.2, R54.1
unnamed: D12.2 (A), R39.2, R42.2
unnamed: R43.2 (S), R47.1
unnamed: R42.1, R43.3 (E)
unnamed: R55.3 (E), R58.1
unnamed: D10.A, R40.1, T2.E
unnamed: LED6.A, R59.2
unnamed: IC8.2 (D), IC8.4 (PRE), IC8.10 (PRE), IC8.12 (D), R34.1
PLL_OUT: IC8.3 (CLK), IC13.4 (O)
V+: C27.1, C28.1, C29.1, C30.1, C31.2, C33.1, C34.2, C36.1, C37.1, IC8.14 (VCC), IC9.5 (VCC), IC10.7 (+VS), IC11.5 (VCC), IC12.5 (VCC), IC13.5 (VCC), IC14.7 (+VS), IC15.7 (+VS), IC16.8 (+VS), LED4.A, R34.2, R40.2, R49.2, R61.2; also elsewhere on the board
V-: C32.1, C35.1, IC14.4 (-VS), IC15.4 (-VS), R39.1; also elsewhere on the board

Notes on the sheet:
npo
SCALE adj. for 0.5V at AD654 pin 4 for 10kHz input
2-pole low-pass filter 0-10kHz -> 0-0.5V nominal 5 kHz -> 0.25 V
AD654 as PLL f-to-v see Analog devices AN278 config for 0.5V in -> 10kHz out input voltage Vss -> (Vcc - 4V) fout = Vin/(10*(R24+R25)*C9)
-2.5V
tune offset to 0
-1 V / 10 kHz 4 Hz / pA
voltage output 1 V/kHz -> 4 mV/pA
tune slope
LM4040 has 35uV typical noise (10 Hz to 10 kHz) At 5 kHz / 0.25 V, that is < 1 Hz equivalent noise

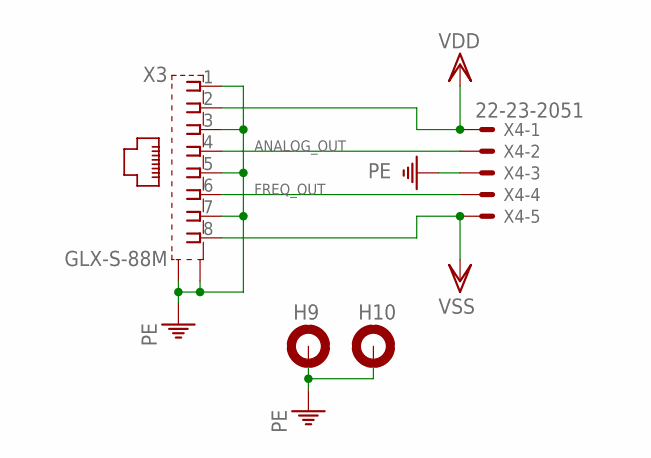
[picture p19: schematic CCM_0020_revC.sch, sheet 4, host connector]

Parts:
H9, H10: MOUNT-PAD-ROUND3.0; 3,0-PAD
X3: GLX-S-88M
X4: 22-23-2051

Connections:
ANALOG_OUT: X3.4, X4.2
FREQ_OUT: X3.6, X4.4
PE: H9.B3,0, H10.B3,0, X3.1, X3.3, X3.5, X3.7, X3.S1, X3.S2, X4.3
VDD: X3.2, X4.1
VSS: X3.8, X4.5

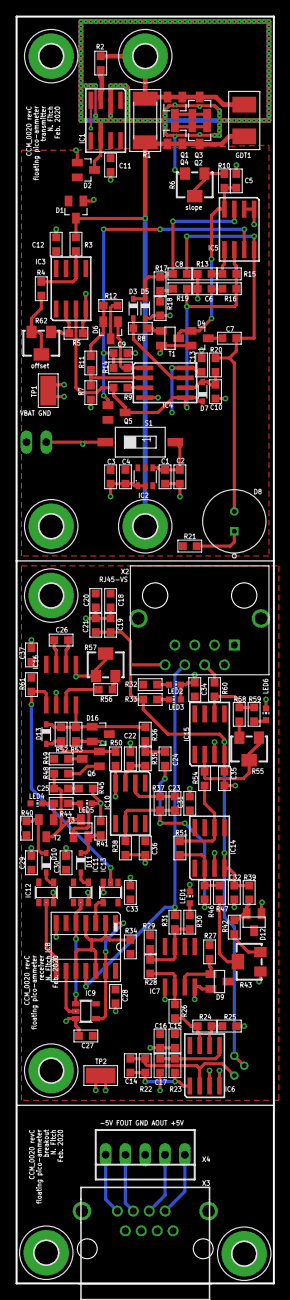
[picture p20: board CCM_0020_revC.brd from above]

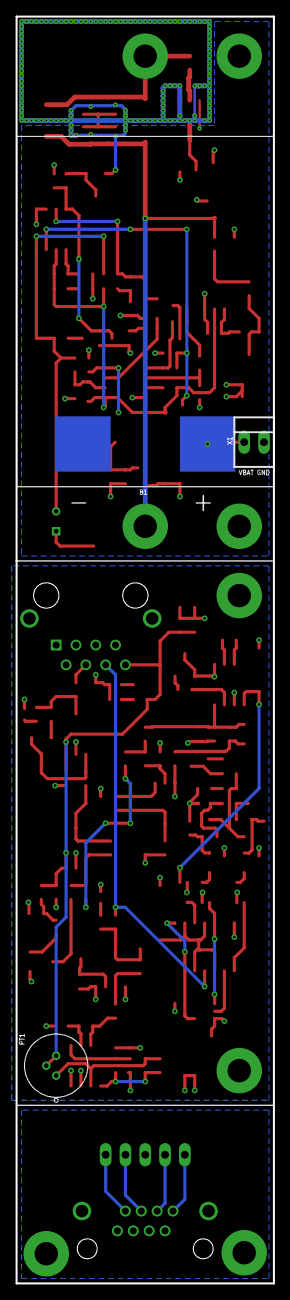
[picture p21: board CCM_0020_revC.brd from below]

Board: 2 copper layers, 33.0 x 162.6 mm, 162 parts (3 on the bottom side), 88 nets.

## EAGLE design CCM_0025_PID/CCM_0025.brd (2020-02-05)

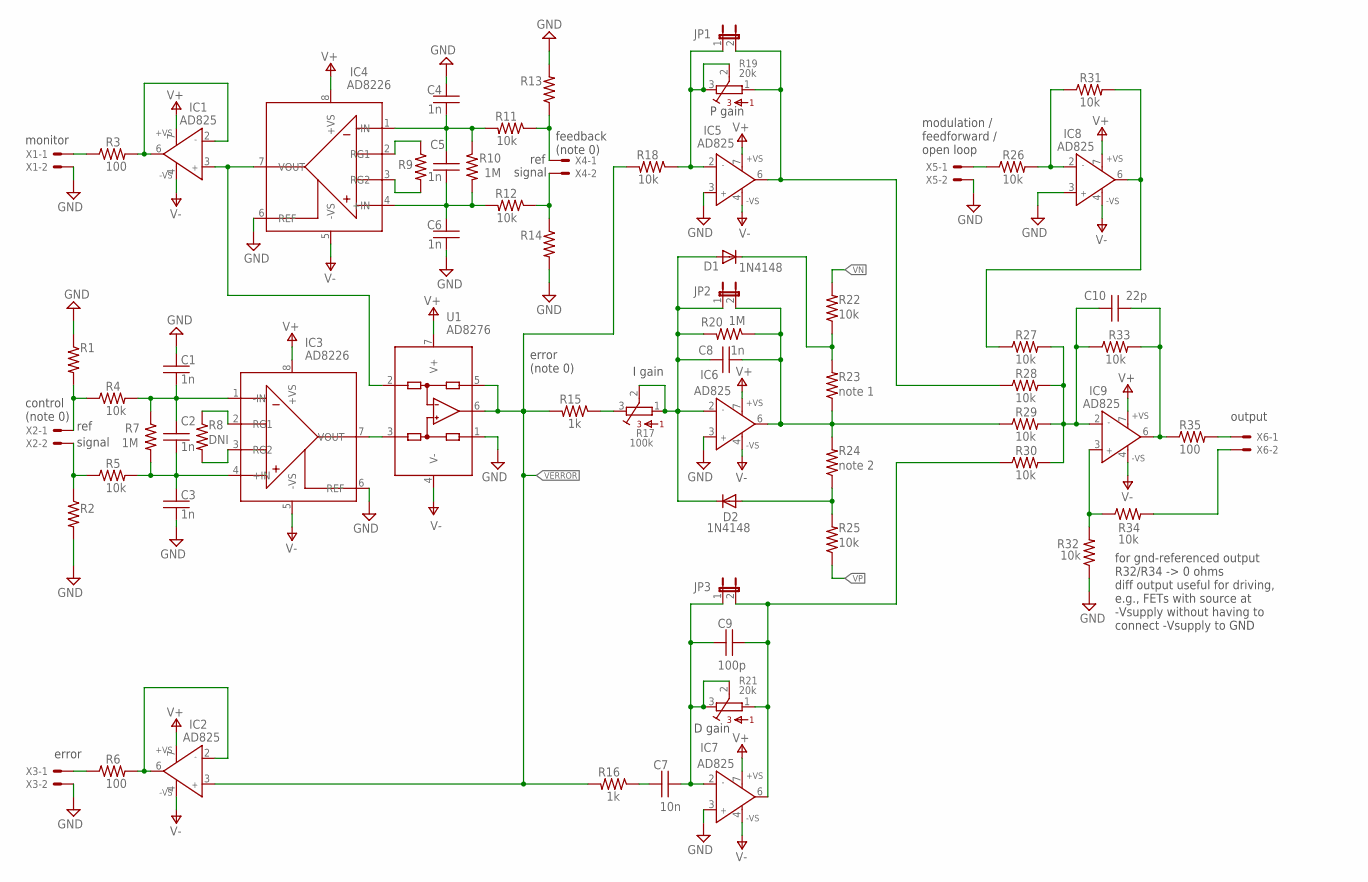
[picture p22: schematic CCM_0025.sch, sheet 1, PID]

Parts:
C1, C2, C3, C4, C5, C6, C8: 1n; 0603
C7: 10n; 0603
C9: 100p; 0603
C10: 22p; 0603
D1, D2: 1N4148; SOD323_ST
IC1, IC2, IC5, IC6, IC7, IC8, IC9: AD825; SO8
IC3, IC4: AD8226; SO08
JP1, JP2, JP3: JP1E; JP1
R1, R2, R4, R5, R11, R12, R13, R14, R18, R22, R25, R26, R27, R28, R29, R30, R31, R32, R33, R34: 10k; 0603
R3, R6, R35: 100; 0603
R7, R10, R20: 1M; 0603
R8, R9: DNI; 0603
R15, R16: 1k; 0603
R17: 100k; 3386C
R19, R21: 20k; 3386C
R23: note 1; 0603
R24: note 2; 0603
U1: AD8276; SO8
X1, X2, X3, X4, X5, X6: 22-23-2021

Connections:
GND: C1.1, C3.2, C4.1, C6.2, IC3.6 (REF), IC4.6 (REF), IC5.3 (IN+), IC6.3 (IN+), IC7.3 (IN+), IC8.3 (IN+), R1.1, R2.2, R13.2, R14.2, R32.1, U1.1 (REF), X1.2, X3.2, X5.2; also elsewhere on the board
unnamed: R2.1, R5.1, X2.2
unnamed: R1.2, R4.1, X2.1
unnamed: C7.1, C9.2, IC7.2 (IN-), JP3.1, R21.2, R21.3
unnamed: IC3.2 (RG1), R8.1
unnamed: C1.2, C2.1, IC3.1 (-IN), R4.2, R7.1
unnamed: C2.2, C3.1, IC3.4 (+IN), R5.2, R7.2
unnamed: R3.1, X1.1
unnamed: IC3.3 (RG2), R8.2
unnamed: IC1.2 (IN-), IC1.6 (OUT), R3.2
unnamed: R26.1, X5.1
unnamed: C9.1, IC7.6 (OUT), JP3.2, R21.1, R30.1
unnamed: C7.2, R16.1
unnamed: R34.2, X6.2
unnamed: C10.2, IC9.2 (IN-), R27.2, R28.2, R29.2, R30.2, R33.1
unnamed: D1.C, R22.1, R23.2
unnamed: C10.1, IC9.6 (OUT), R33.2, R35.1
unnamed: IC9.3 (IN+), R32.2, R34.1
unnamed: R35.2, X6.1
unnamed: IC3.7 (VOUT), U1.3 (+IN)
unnamed: R12.1, R14.1, X4.2
unnamed: IC4.2 (RG1), R9.1
unnamed: IC4.3 (RG2), R9.2
unnamed: C4.2, C5.1, IC4.1 (-IN), R10.1, R11.2
unnamed: C5.2, C6.1, IC4.4 (+IN), R10.2, R12.2
unnamed: R11.1, R13.1, X4.1
unnamed: IC5.2 (IN-), JP1.1, R18.1, R19.2, R19.3
unnamed: IC5.6 (OUT), JP1.2, R19.1, R28.1
unnamed: R15.1, R17.3
unnamed: C8.2, D1.A, D2.C, IC6.2 (IN-), JP2.1, R17.1, R17.2, R20.2
unnamed: D2.A, R24.1, R25.2
unnamed: C8.1, IC6.6 (OUT), JP2.2, R20.1, R23.1, R24.2, R29.1
unnamed: IC1.3 (IN+), IC4.7 (VOUT), U1.2 (-IN)
unnamed: R6.1, X3.1
unnamed: IC2.2 (IN-), IC2.6 (OUT), R6.2
unnamed: IC8.2 (IN-), R26.2, R31.1
unnamed: IC8.6 (OUT), R27.1, R31.2
V+: IC1.7 (+VS), IC2.7 (+VS), IC3.8 (+VS), IC4.8 (+VS), IC5.7 (+VS), IC6.7 (+VS), IC7.7 (+VS), IC8.7 (+VS), IC9.7 (+VS), U1.7 (V+); also elsewhere on the board
V-: IC1.4 (-VS), IC2.4 (-VS), IC3.5 (-VS), IC4.5 (-VS), IC5.4 (-VS), IC6.4 (-VS), IC7.4 (-VS), IC8.4 (-VS), IC9.4 (-VS), U1.4 (V-); also elsewhere on the board
VERROR: IC2.3 (IN+), R15.2, R16.2, R18.2, U1.5 (SENSE), U1.6 (OUT)
VN: R22.2; also elsewhere on the board
VP: R25.1; also elsewhere on the board

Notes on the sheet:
control (note 0)
monitor
signal
ref
feedback (note 0)
error
P gain
I gain
D gain
modulation / feedforward / open loop
output
error (note 0)
for gnd-referenced output R32/R34 -> 0 ohms diff output useful for driving, e.g., FETs with source at -Vsupply without having to connect -Vsupply to GND

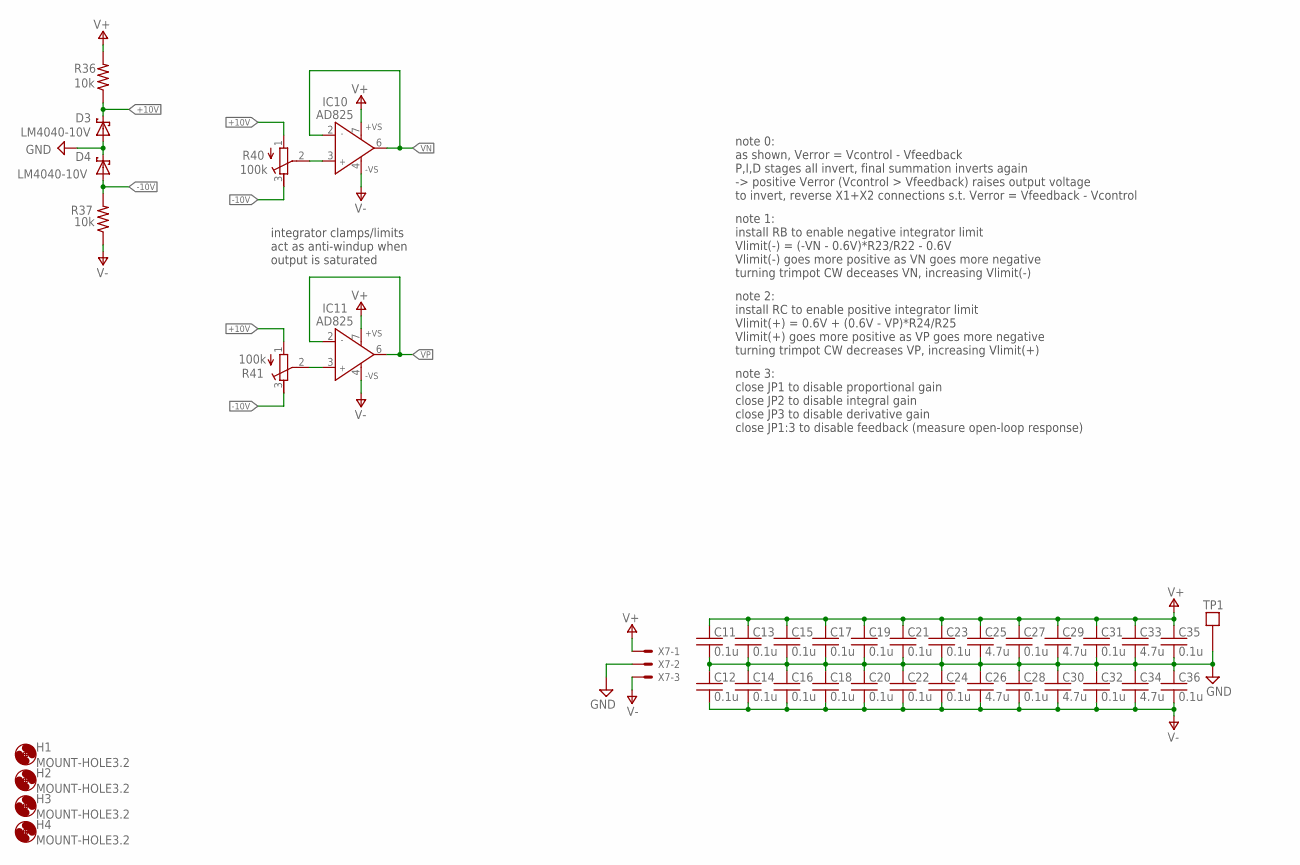
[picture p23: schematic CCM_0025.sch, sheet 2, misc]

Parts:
C11, C12, C13, C14, C15, C16, C17, C18, C19, C20, C21, C22, C23, C24, C27, C28, C31, C32, C35, C36: 0.1u; 0603
C25, C26, C29, C30, C33, C34: 4.7u; 0603
D3, D4: LM4040-10V; SOT23
H1, H2, H3, H4: MOUNT-HOLE3.2; 3,2
IC10, IC11: AD825; SO8
R36, R37: 10k; 0603
R40, R41: 100k; RTRIM3296W
TP1: TESTPOINT
X7: 22-23-2031

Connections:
+10V: D3.1 (C), R36.1, R40.1 (A), R41.1 (A)
-10V: D4.2 (A), R37.2, R40.3 (E), R41.3 (E)
GND: C11.2, C12.1, C13.2, C14.1, C15.2, C16.1, C17.2, C18.1, C19.2, C20.1, C21.2, C22.1, C23.2, C24.1, C25.2, C26.1, C27.2, C28.1, C29.2, C30.1, C31.2, C32.1, C33.2, C34.1, C35.2, C36.1, D3.2 (A), D4.1 (C), TP1.P$1, X7.2; also elsewhere on the board
unnamed: IC10.3 (IN+), R40.2 (S)
unnamed: IC11.3 (IN+), R41.2 (S)
V+: C11.1, C13.1, C15.1, C17.1, C19.1, C21.1, C23.1, C25.1, C27.1, C29.1, C31.1, C33.1, C35.1, IC10.7 (+VS), IC11.7 (+VS), R36.2, X7.1; also elsewhere on the board
V-: C12.2, C14.2, C16.2, C18.2, C20.2, C22.2, C24.2, C26.2, C28.2, C30.2, C32.2, C34.2, C36.2, IC10.4 (-VS), IC11.4 (-VS), R37.1, X7.3; also elsewhere on the board
VN: IC10.2 (IN-), IC10.6 (OUT); also elsewhere on the board
VP: IC11.2 (IN-), IC11.6 (OUT); also elsewhere on the board

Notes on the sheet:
integrator clamps/limits act as anti-windup when output is saturated
note 1: install RB to enable negative integrator limit Vlimit(-) = (-VN - 0.6V)*R23/R22 - 0.6V Vlimit(-) goes more positive as VN goes more negative turning trimpot CW deceases VN, increasing Vlimit(-)
note 2: install RC to enable positive integrator limit Vlimit(+) = 0.6V + (0.6V - VP)*R24/R25 Vlimit(+) goes more positive as VP goes more negative turning trimpot CW decreases VP, increasing Vlimit(+)
note 3: close JP1 to disable proportional gain close JP2 to disable integral gain close JP3 to disable derivative gain close JP1:3 to disable feedback (measure open-loop response)
note 0: as shown, Verror = Vcontrol - Vfeedback P,I,D stages all invert, final summation inverts again -> positive Verror (Vcontrol > Vfeedback) raises output voltage to invert, reverse X1+X2 connections s.t. Verror = Vfeedback - Vcontrol

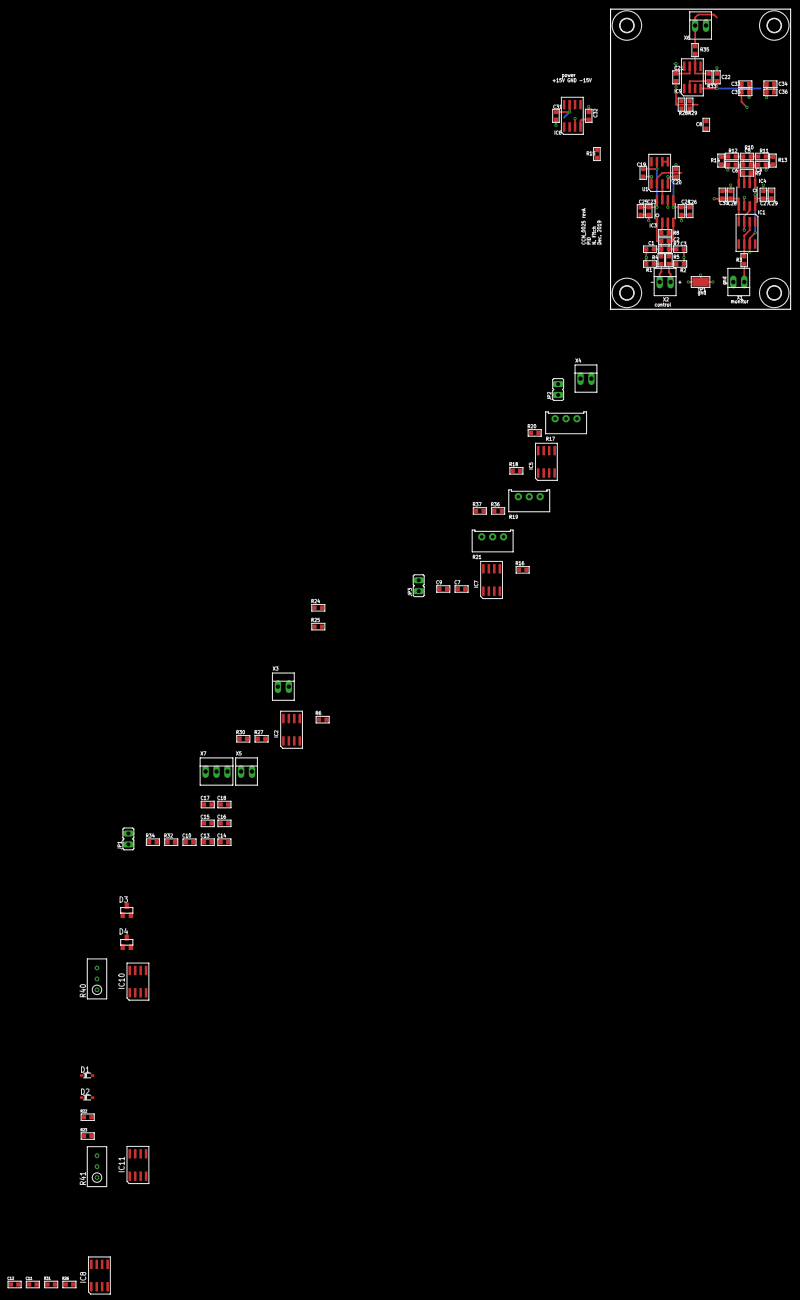
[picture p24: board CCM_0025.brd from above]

Board: 2 copper layers, 41.9 x 69.8 mm, 106 parts (0 on the bottom side), 46 nets.

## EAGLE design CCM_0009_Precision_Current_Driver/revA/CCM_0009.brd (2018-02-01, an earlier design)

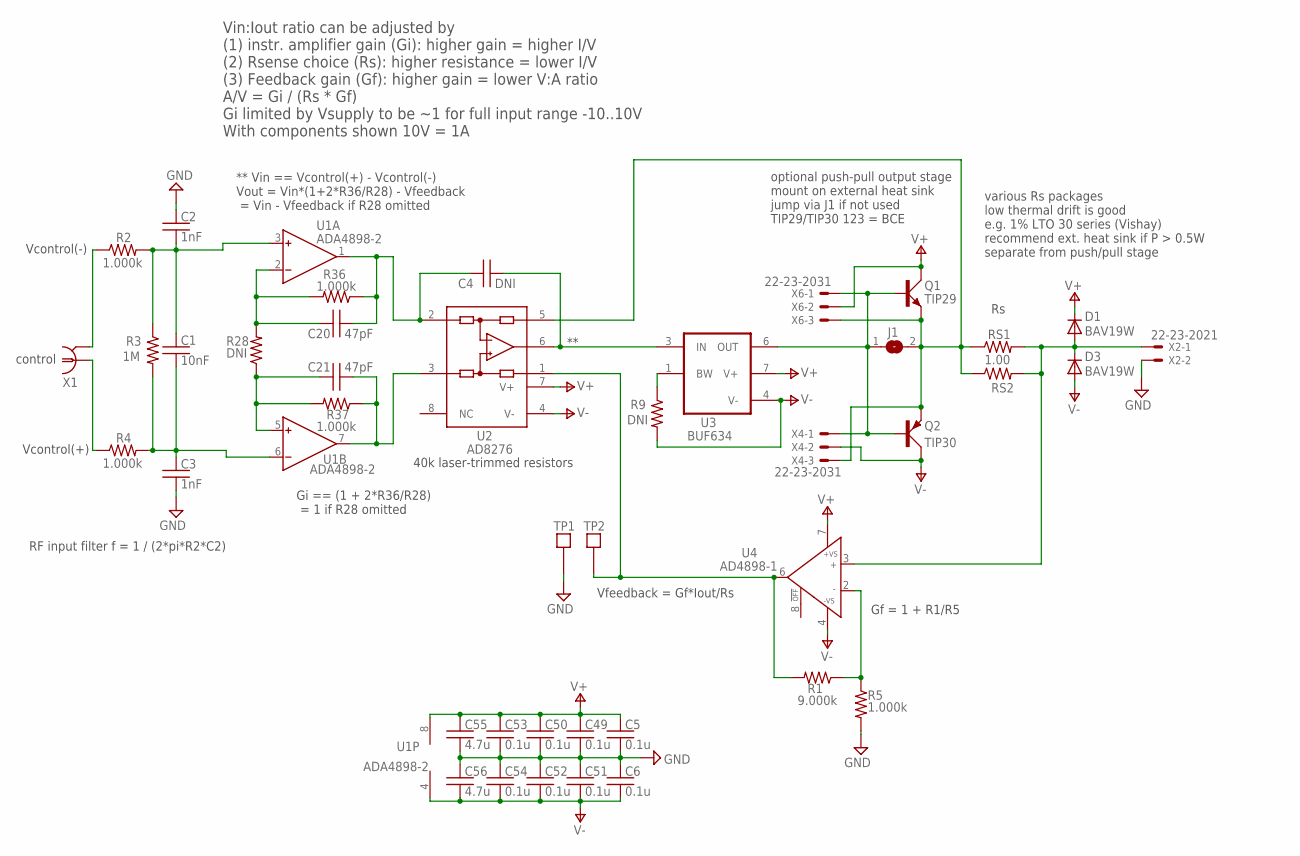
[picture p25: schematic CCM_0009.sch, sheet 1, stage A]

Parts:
C1: 10nF; 0603
C2, C3: 1nF; 0603
C4: DNI; 0603
C5, C6, C49, C50, C51, C52, C53, C54: 0.1u; 0603
C20, C21: 47pF; 0603
C55, C56: 4.7u; 0603
D1, D3: BAV19W; SOD123
J1: SJ
Q1: TIP29; TO220AV
Q2: TIP30; TO220AV
R1: 9.000k; 0603
R2, R4, R5, R36, R37: 1.000k; 0603
R3: 1M; 0603
R9, R28: DNI; 0603
RS1: 1.00; LTO30
RS2: DNI; 2512
TP1, TP2: TESTPOINT
U1: ADA4898-2; SO8
U2: AD8276; SO8
U3: BUF634; SO8
U4: AD4898-1; SO8
X1: 1-227161-0; AMP_227161
X2: 22-23-2021
X4, X6: 22-23-2031

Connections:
GND: C2.1, C3.2, C5.2, C6.1, C49.2, C50.2, C51.1, C52.1, C53.2, C54.1, C55.2, C56.1, R5.2, TP1.P$1, X2.2; also elsewhere on the board
unnamed: R2.1, X1.2
unnamed: R4.1, X1.1
unnamed: C4.2, U2.6 (OUT), U3.3 (IN)
unnamed: C1.1, C2.2, R2.2, R3.1, U1.3 (IN+)
unnamed: C1.2, C3.1, R3.2, R4.2, U1.6 (IN-)
unnamed: R1.1, R5.1, U4.2 (IN-)
unnamed: J1.1, Q1.B, Q2.B, U3.6 (OUT), X4.1, X6.1
unnamed: D1.A, D3.C, RS1.P$2 (2), RS2.2, U4.3 (IN+), X2.1
unnamed: J1.2, Q1.E, Q2.E, RS1.P$1 (1), RS2.1, U2.5 (SENSE), X4.3, X6.3
unnamed: R9.1, U3.1 (BW)
unnamed: R1.2, TP2.P$1, U2.1 (REF), U4.6 (OUT)
unnamed: C20.1, R28.2, R36.2, U1.2 (IN-)
unnamed: C21.1, R28.1, R37.2, U1.5 (IN+)
unnamed: C21.2, R37.1, U1.7 (OUT), U2.3 (+IN)
unnamed: C4.1, C20.2, R36.1, U1.1 (OUT), U2.2 (-IN)
V+: C5.1, C49.1, C50.1, C53.1, C55.1, D1.C, Q1.C, U1.8 (V+), U2.7 (V+), U3.7 (V+), U4.7 (+VS), X6.2; also elsewhere on the board
V-: C6.2, C51.2, C52.2, C54.2, C56.2, D3.A, Q2.C, R9.2, U1.4 (V-), U2.4 (V-), U3.4 (V-), U4.4 (-VS), X4.2; also elsewhere on the board

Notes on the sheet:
control
RF input filter f = 1 / (2*pi*R2*C2)
optional push-pull output stage mount on external heat sink jump via J1 if not used TIP29/TIP30 123 = BCE
40k laser-trimmed resistors
Vcontrol(+)
Vcontrol(-)
various Rs packages low thermal drift is good e.g. 1% LTO 30 series (Vishay) recommend ext. heat sink if P > 0.5W separate from push/pull stage
** Vin == Vcontrol(+) - Vcontrol(-) Vout = Vin*(1+2*R36/R28) - Vfeedback = Vin - Vfeedback if R28 omitted
Gi == (1 + 2*R36/R28) = 1 if R28 omitted
Vfeedback = Gf*Iout/Rs
Gf = 1 + R1/R5
Vin:Iout ratio can be adjusted by (1) instr. amplifier gain (Gi): higher gain = higher I/V (2) Rsense choice (Rs): higher resistance = lower I/V (3) Feedback gain (Gf): higher gain = lower V:A ratio A/V = Gi / (Rs * Gf) Gi limited by Vsupply to be ~1 for full input range -10..10V With components sh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

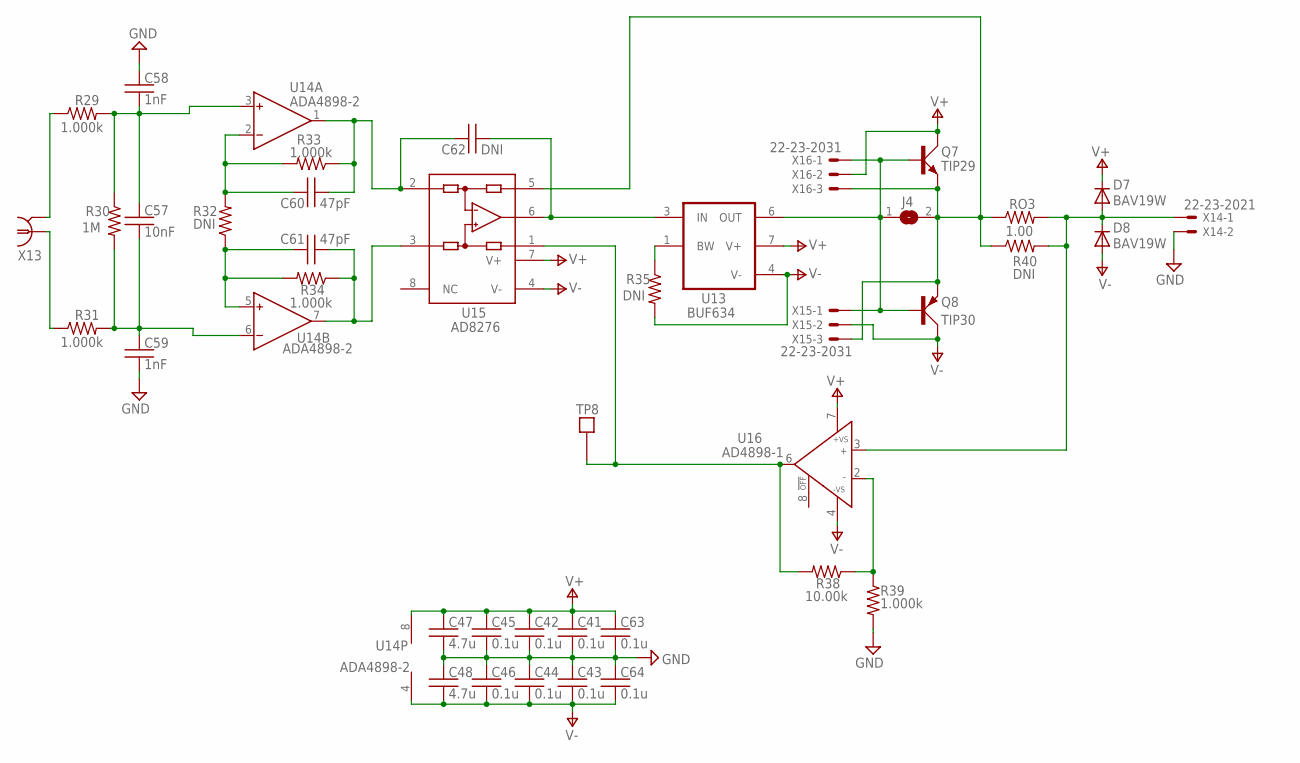
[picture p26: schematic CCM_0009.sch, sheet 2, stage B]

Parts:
C41, C42, C43, C44, C45, C46, C63, C64: 0.1u; 0603
C47, C48: 4.7u; 0603
C57: 10nF; 0603
C58, C59: 1nF; 0603
C60, C61: 47pF; 0603
C62: DNI; 0603
D7, D8: BAV19W; SOD123
J4: SJ
Q7: TIP29; TO220AV
Q8: TIP30; TO220AV
R29, R31, R33, R34, R39: 1.000k; 0603
R30: 1M; 0603
R32, R35: DNI; 0603
R38: 10.00k; 0603
R40: DNI; 2512
RO3: 1.00; LTO30
TP8: TESTPOINT
U13: BUF634; SO8
U14: ADA4898-2; SO8
U15: AD8276; SO8
U16: AD4898-1; SO8
X13: 1-227161-0; AMP_227161
X14: 22-23-2021
X15, X16: 22-23-2031

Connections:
GND: C41.2, C42.2, C43.1, C44.1, C45.2, C46.1, C47.2, C48.1, C58.1, C59.2, C63.2, C64.1, R39.2, X14.2; also elsewhere on the board
unnamed: C57.1, C58.2, R29.2, R30.1, U14.3 (IN+)
unnamed: C57.2, C59.1, R30.2, R31.2, U14.6 (IN-)
unnamed: R29.1, X13.2
unnamed: R31.1, X13.1
unnamed: C60.1, R32.2, R33.2, U14.2 (IN-)
unnamed: C61.1, R32.1, R34.2, U14.5 (IN+)
unnamed: C61.2, R34.1, U14.7 (OUT), U15.3 (+IN)
unnamed: C60.2, C62.1, R33.1, U14.1 (OUT), U15.2 (-IN)
unnamed: J4.1, Q7.B, Q8.B, U13.6 (OUT), X15.1, X16.1
unnamed: D7.A, D8.C, R40.2, RO3.P$2 (2), U16.3 (IN+), X14.1
unnamed: R35.1, U13.1 (BW)
unnamed: C62.2, U13.3 (IN), U15.6 (OUT)
unnamed: R38.2, TP8.P$1, U15.1 (REF), U16.6 (OUT)
unnamed: J4.2, Q7.E, Q8.E, R40.1, RO3.P$1 (1), U15.5 (SENSE), X15.3, X16.3
unnamed: R38.1, R39.1, U16.2 (IN-)
V+: C41.1, C42.1, C45.1, C47.1, C63.1, D7.C, Q7.C, U13.7 (V+), U14.8 (V+), U15.7 (V+), U16.7 (+VS), X16.2; also elsewhere on the board
V-: C43.2, C44.2, C46.2, C48.2, C64.2, D8.A, Q8.C, R35.2, U13.4 (V-), U14.4 (V-), U15.4 (V-), U16.4 (-VS), X15.2; also elsewhere on the board

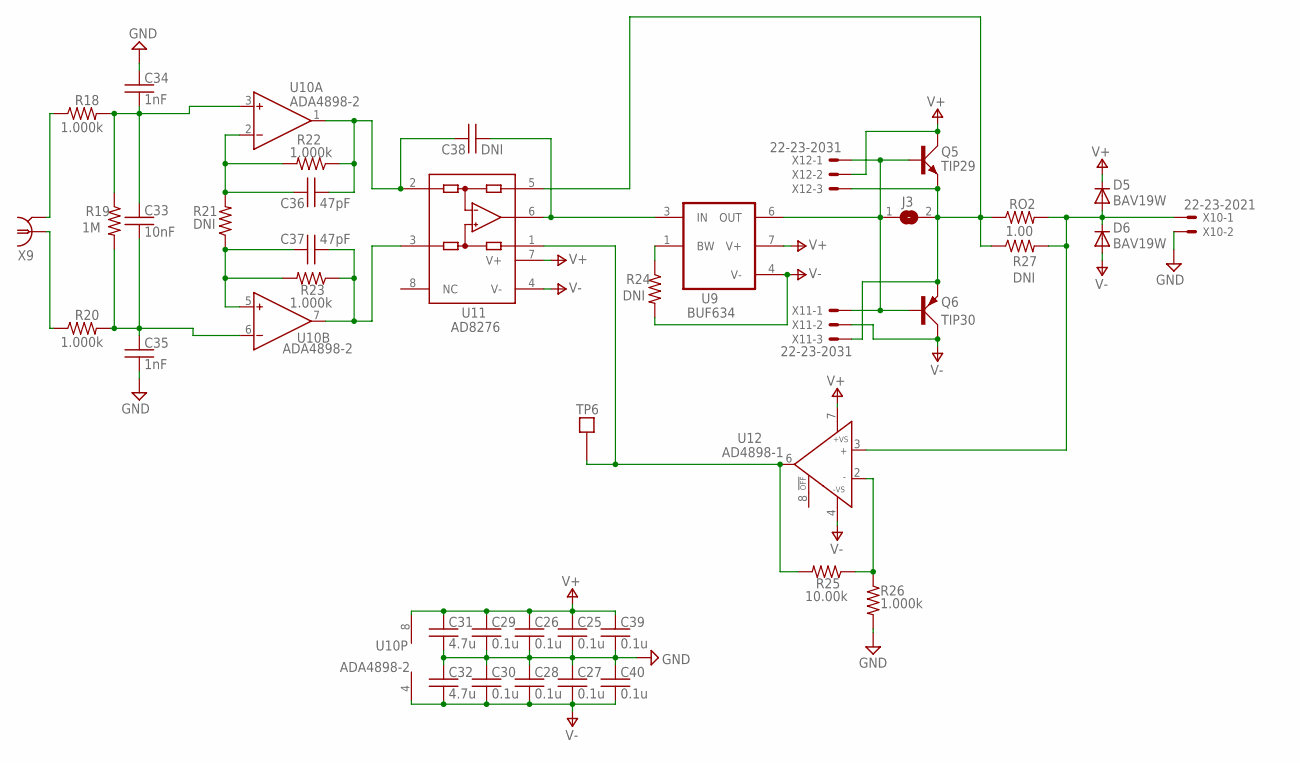
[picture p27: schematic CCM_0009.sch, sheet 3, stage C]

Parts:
C25, C26, C27, C28, C29, C30, C39, C40: 0.1u; 0603
C31, C32: 4.7u; 0603
C33: 10nF; 0603
C34, C35: 1nF; 0603
C36, C37: 47pF; 0603
C38: DNI; 0603
D5, D6: BAV19W; SOD123
J3: SJ
Q5: TIP29; TO220AV
Q6: TIP30; TO220AV
R18, R20, R22, R23, R26: 1.000k; 0603
R19: 1M; 0603
R21, R24: DNI; 0603
R25: 10.00k; 0603
R27: DNI; 2512
RO2: 1.00; LTO30
TP6: TESTPOINT
U9: BUF634; SO8
U10: ADA4898-2; SO8
U11: AD8276; SO8
U12: AD4898-1; SO8
X9: 1-227161-0; AMP_227161
X10: 22-23-2021
X11, X12: 22-23-2031

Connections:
GND: C25.2, C26.2, C27.1, C28.1, C29.2, C30.1, C31.2, C32.1, C34.1, C35.2, C39.2, C40.1, R26.2, X10.2; also elsewhere on the board
unnamed: C33.1, C34.2, R18.2, R19.1, U10.3 (IN+)
unnamed: C33.2, C35.1, R19.2, R20.2, U10.6 (IN-)
unnamed: R18.1, X9.2
unnamed: R20.1, X9.1
unnamed: C36.1, R21.2, R22.2, U10.2 (IN-)
unnamed: C37.1, R21.1, R23.2, U10.5 (IN+)
unnamed: C37.2, R23.1, U10.7 (OUT), U11.3 (+IN)
unnamed: C36.2, C38.1, R22.1, U10.1 (OUT), U11.2 (-IN)
unnamed: J3.1, Q5.B, Q6.B, U9.6 (OUT), X11.1, X12.1
unnamed: D5.A, D6.C, R27.2, RO2.P$2 (2), U12.3 (IN+), X10.1
unnamed: R24.1, U9.1 (BW)
unnamed: C38.2, U9.3 (IN), U11.6 (OUT)
unnamed: R25.2, TP6.P$1, U11.1 (REF), U12.6 (OUT)
unnamed: J3.2, Q5.E, Q6.E, R27.1, RO2.P$1 (1), U11.5 (SENSE), X11.3, X12.3
unnamed: R25.1, R26.1, U12.2 (IN-)
V+: C25.1, C26.1, C29.1, C31.1, C39.1, D5.C, Q5.C, U9.7 (V+), U10.8 (V+), U11.7 (V+), U12.7 (+VS), X12.2; also elsewhere on the board
V-: C27.2, C28.2, C30.2, C32.2, C40.2, D6.A, Q6.C, R24.2, U9.4 (V-), U10.4 (V-), U11.4 (V-), U12.4 (-VS), X11.2; also elsewhere on the board


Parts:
C7, C9: 4.7u; 0603
C8, C24: 0.1u; 0603
X5, X7: 22-23-2031

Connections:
GND: C7.2, C8.2, C9.1, C24.1, X5.2, X7.2; also elsewhere on the board
V+: C7.1, C8.1, X5.1, X7.1; also elsewhere on the board
V-: C9.2, C24.2, X5.3, X7.3; also elsewhere on the board

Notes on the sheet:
Power off +/-5V to +/-15V use lowest practical supply voltage to reduce output stage power dissipation

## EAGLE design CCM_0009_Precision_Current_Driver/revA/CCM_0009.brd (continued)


Board: 2 copper layers, 82.5 x 76.2 mm, 130 parts (0 on the bottom side), 48 nets.

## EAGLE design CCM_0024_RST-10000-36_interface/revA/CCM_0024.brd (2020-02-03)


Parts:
LED1: green; LED_SML0603
LED2: red; LED_SML0603
LED3: yellow; LED_SML0603
LED4: orange; LED_SML0603
R1, R4: 120k; 0603
R2, R5: 100k; RTRIM3296Y
R3, R6: 20k; 0603
R7, R8, R9, R10: 10k; 0603
TP1: TESTPOINT
X1: 22-23-2021
X2: 87758-1016
X3: 87758-2016
X4: F09V

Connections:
12V-AUX: R1.1, R4.1, R7.1, R8.1, R9.1, R10.1, X3.1, X4.2
+S: X1.1, X2.3
+V: X3.5, X4.1
-S: X1.2, X2.5
AC-FAIL1: X3.19
AC-FAIL2: LED2.C, X3.8, X4.7
CS+: X2.2
CS-: X2.1
DC-OK1: X3.14
DC-OK2: LED1.C, X3.4, X4.8
FAN-FAIL1: X3.20
FAN-FAIL2: LED3.C, X3.10, X4.4
GND: R3.2, R6.2, TP1.P$1, X2.4, X2.7, X2.8, X3.2, X3.3, X3.6, X3.7, X3.11, X3.12, X3.15, X3.16, X3.17, X3.18, X4.3
unnamed: LED1.A, R7.2
unnamed: R2.1 (A), R3.1
unnamed: R1.2, R2.3 (E)
unnamed: LED2.A, R8.2
unnamed: LED3.A, R9.2
unnamed: LED4.A, R10.2
unnamed: R5.1 (A), R6.1
unnamed: R4.2, R5.3 (E)
OTP1: X3.13
OTP2: LED4.C, X3.9, X4.6
PC+: R5.2 (S), X2.9
PV+: R2.2 (S), X2.6
RC+: X2.10, X4.5

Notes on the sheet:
CN991
CN992
CS- CS+ +S PV- -S PV+ PC- RC- PC+ RC+
12V-AUX DC-OK2-GND GND-AUX DC-OK2 +V AC-FAIL2-GND -V AC-FAIL2 OTP2 FAN-FAIL2 OTP2-GND FAN-FAIL2-GND OTP1 DC-OK1 OTP1-GND DC-OK1-GND AC-FAIL1-GND FAN-FAIL1-GND AC-FAIL1 FAN-FAIL1
to supply terminals or load sense


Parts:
Q1: MMBT3906; SOT23-BEC
R11, R12, R13, R14, R17, R18: 2k; 0603
R21: 10k; 0603
X7: F09H
X10, X11: 22-23-2021
X13: 22-23-2061

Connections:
!AC_FAIL: R14.2, X7.7
!DC_OK: R18.2, X7.8
!FAN_FAIL: R13.2, X7.4
!OTP: R17.2, X7.6
+12V: X7.2, X10.1, X13.1
AGND: Q1.C, R21.2, X7.3, X11.2
ENABLE: R12.1, R21.1, X7.5, X10.2
unnamed: R11.1, X13.6
unnamed: Q1.E, R11.2
unnamed: R17.1, X13.2
unnamed: Q1.B, R12.2
unnamed: R14.1, X13.3
unnamed: R13.1, X13.5
unnamed: R18.1, X13.4
VMON: X7.1, X11.1

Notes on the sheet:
interlock(s) close to enable
connect to enable supply
indicator led anodes dc ok led cathode ac fail led cathode otp led cathode fan fail led cathode interlock led cathode



Board: 2 copper layers, 33.0 x 64.8 mm, 31 parts (2 on the bottom side), 35 nets.

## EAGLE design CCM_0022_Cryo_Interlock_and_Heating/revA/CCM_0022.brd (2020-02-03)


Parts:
C1, C4: 4.7u; 0603
C2, C3, C5, C9: 0.1u; 0603
D1, D2, D5, D6, D7, D8: HLMP6
D3: BZX84; TO236
D4: 1N4148; SOD323-W
IC1: 741G3157DBVR; DBV_R-PDSO-G6
IC6: 74AHC1G125DBV; SOT23-5
IC7: ZXTR2105F; SOT23
Q1, Q2: 2N7002; SOT23
R1, R24: 100k; 0603
R2, R3, R5, R6, R7, R8: 5.1k; 0603
R4: 10k; 0603
S1, S2: LPV-1
X1: BNC-8; BNC_RA
X2: 22-23-2021
X3: Male DB15; M15HP

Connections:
+5V: C3.1, C4.1, C5.1, C9.1, IC1.5 (VCC), IC6.5 (VCC), IC7.2 (VO), R24.2, S1.1 (O), S2.1 (O); also elsewhere on the board
+24V: C1.1, C2.1, D4.C, IC7.3 (VI), R2.2, R3.2, R6.2, R7.2, R8.2, X3.13
COOLER_ON: R5.2, X3.6
CRYO_ON: D3.C, IC6.4 (O), Q2.1 (G), R4.2; also elsewhere on the board
GND: C1.2, C2.2, C3.2, C4.2, C5.2, C9.2, D2.K, D3.A, D5.K, D6.K, D7.K, D8.K, IC1.2 (GND), IC6.3 (GND), IC7.1 (GND), Q1.2 (S), Q2.2 (S), R1.1, R4.1, S1.3 (S), S1.B, S1.B1, S2.3 (S), S2.B, S2.B1, X1.2, X2.2, X3.2, X3.4, X3.7, X3.9, X3.11, X3.15; also elsewhere on the board
HELIUM_DISCHARGE_TEMP: D7.A, R7.1, X3.3
HELIUM_INLET_TEMP: D6.A, R6.1, X3.5
MANUAL/!REMOTE: IC1.6 (!A!/B), S1.2; also elsewhere on the board
unnamed: D1.A, R2.1
unnamed: IC6.1 (OE), Q1.1 (G), R24.1, X2.1
unnamed: D1.K, Q1.3 (D)
unnamed: IC1.4 (X), IC6.2 (I)
unnamed: D5.A, R5.1
unnamed: D4.A, Q2.3 (D), X3.8
unnamed: IC1.3 (A), R1.2, X1.1
unnamed: IC1.1 (B), S2.2
PRESSURE_ALARM: D8.A, R8.1, X3.1
WATER_OVER_TEMP: D2.A, R3.1, X3.10


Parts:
C6, C7, C8: 0.1u; 0603
D11, D12, D13, D14, D17, D18: BZX84; TO236
D15, D16, D19: HLMP6
IC3, IC4, IC5: 741G3157DBVR; DBV_R-PDSO-G6
Q3, Q4, Q6, Q8, Q11: 2N7002; SOT23
Q5, Q14, Q15: BSP613P; SOT223
R9, R10, R19: 1k; 0603
R11, R12, R20: 10k; 0603
R13, R15, R21: 1.5k; 0603
R14, R16, R22: 3.6k; 0603
R25, R26, R27: 100k; 0603
S3, S4, S5: LPV-1
X4, X5, X8: BNC-8; BNC_RA
X13, X14, X15: 22-23-2031

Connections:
+5V: C6.1, C7.1, C8.1, IC3.5 (VCC), IC4.5 (VCC), IC5.5 (VCC), S3.1 (O), S4.1 (O), S5.1 (O); also elsewhere on the board
CRYO_ON: Q6.3 (D), Q8.3 (D); also elsewhere on the board
GND: C6.2, C7.2, C8.2, D11.A, D12.A, D17.A, IC3.2 (GND), IC4.2 (GND), IC5.2 (GND), Q3.2 (S), Q4.2 (S), Q6.2 (S), Q8.2 (S), Q11.2 (S), R11.1, R12.1, R20.1, R25.1, R26.1, R27.1, S3.3 (S), S3.B, S3.B1, S4.3 (S), S4.B, S4.B1, S5.3 (S), S5.B, S5.B1, X4.2, X5.2, X8.2, X13.3, X14.3, X15.3; also elsewhere on the board
MANUAL/!REMOTE: IC3.6 (!A!/B), IC4.6 (!A!/B), IC5.6 (!A!/B); also elsewhere on the board
unnamed: D13.C, Q14.3 (S), R13.2, X15.1
unnamed: D14.C, Q5.3 (S), R15.2, X13.1
unnamed: D16.A, R16.1
unnamed: D16.K, Q4.3 (D)
unnamed: D19.K, Q11.3 (D)
unnamed: D19.A, R22.1
unnamed: D15.K, Q3.3 (D)
unnamed: D15.A, R14.1
unnamed: D11.C, Q3.1 (G), Q6.1 (G), R9.1, R11.2
unnamed: D13.A, Q14.1 (G), R13.1, R14.2
unnamed: Q14.2 (D), Q14.4 (D), X15.2
unnamed: D12.C, Q4.1 (G), Q8.1 (G), R10.1, R12.2
unnamed: D14.A, Q5.1 (G), R15.1, R16.2
unnamed: Q5.2 (D), Q5.4 (D), X13.2
unnamed: IC4.3 (A), R26.2, X5.1
unnamed: IC4.1 (B), S4.2
unnamed: D17.C, Q11.1 (G), R19.1, R20.2
unnamed: D18.A, Q15.1 (G), R21.1, R22.2
unnamed: Q15.2 (D), Q15.4 (D), X14.2
unnamed: IC3.3 (A), R25.2, X4.1
unnamed: IC3.1 (B), S3.2
unnamed: IC5.3 (A), R27.2, X8.1
unnamed: IC5.1 (B), S5.2
S1_HEATER_ON/!OFF: IC3.4 (X), R9.2
S1_HEATER_ON/!OFF1: IC4.4 (X), R10.2
S1_HEATER_ON/!OFF2: IC5.4 (X), R19.2
SF6_HEATER_VOLTAGE: D18.C, Q15.3 (S), R21.2, X14.1

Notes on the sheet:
to 1st stage (S1) heater (rear panel)
heater elements are typically 25 ohms 1A (25W) heating power nominal Each heater has independent power connections allowing either independent supplies to be used or the heating rates to be adjusted/matched using, e.g., diode drops etc. from a single supply. Enabling either the S1 or S2 heater(s) d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
to 2nd stage (S2) heater (rear panel)
to SF6 heater (rear panel)


Board: 2 copper layers, 203.2 x 42.7 mm, 80 parts (1 on the bottom side), 45 nets.

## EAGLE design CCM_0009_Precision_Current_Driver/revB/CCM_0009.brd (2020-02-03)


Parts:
C1, C2, C3, C4, C10, C12: 0.1u; 0603
C5, C6, C9, C11: 4.7u; 0603
C7: 10n; 0603
C8: 100p; 0603
D1, D2: 1N4148; SOD323_ST
H1, H2, H3, H4: MOUNT-HOLE3.0; 3,0
IC1: AD8620R; SO8
R1, R2, R4, R12, R13: 10k; 0603
R3, R7: 100; 0603
R5: DNI; 0603
R6: 190k; 0603
R8, R9: 490; 0603
R10, R11: 1; LTO30
R14: 0.5; LTO30
T1: TIP29; TO220V
T2: TIP30; TO220V
TP1: TESTPOINT
X1, X2, X6: 22-23-2031
X3, X4, X5: 22-23-2021

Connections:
+5V: C9.1, C10.1, R8.1, T1.2 (C), X6.1
-5V: C11.2, C12.2, R9.2, T2.2 (C), X6.3
B: R12.1, R14.P$2 (2), X5.2
GND: C1.2, C2.1, C3.2, C4.1, C5.2, C6.1, C9.2, C10.2, C11.1, C12.1, R1.2, R13.1, R14.P$1 (1), TP1.P$1, X1.2, X2.2, X3.2, X4.2, X6.2
unnamed: R11.P$1 (1), T2.3 (E)
unnamed: R10.P$1 (1), R11.P$2 (2), X5.1
unnamed: R10.P$2 (2), T1.3 (E)
unnamed: C7.2, IC1.1 (OUT), R5.1, R7.2
unnamed: IC1.5 (IN+), R12.2
unnamed: C8.2, IC1.6 (IN-), R6.1, R13.2
unnamed: D1.A, R8.2, T1.1 (B)
unnamed: R3.2, X4.1
unnamed: C8.1, IC1.7 (OUT), R3.1, R4.2, R6.2
unnamed: D1.C, D2.A, R7.1
unnamed: C7.1, IC1.2 (IN-), R4.1
unnamed: IC1.3 (IN+), R2.1, R5.2
unnamed: D2.C, R9.1, T2.1 (B)
unnamed: R1.1, R2.2, X3.1
V+: C1.1, C3.1, C5.1, IC1.8 (V+), X1.1, X2.1
V-: C2.2, C4.2, C6.2, IC1.4 (V-), X1.3, X2.3

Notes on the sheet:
control
configure circuit for desired current range Iout = (Vin*Gin) / (Rs*Gf) nominal Vin of 0..10V (unipolar) or -10V..10V (bipolar) so Gin->1 values shown give Gf~100 100mA bipolar: R13->1, R9/R10->10 jump X5, load on X6 1A bipolar: R9/R10->1, R16->0.1 requires good heatsinking of T1/T2
monitor
to load


Board: 2 copper layers, 45.7 x 45.7 mm, 42 parts (0 on the bottom side), 20 nets.

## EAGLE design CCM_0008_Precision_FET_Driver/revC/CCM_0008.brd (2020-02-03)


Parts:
C1, C2, C6, C7, C8, C9, C12, C13, C16, C17, C20, C21: 0.1u; 0603
C3, C5, C24, C26, C27, C28: 1nF; 0603
C4: 10nF; 0603
C10, C11, C14, C15, C18, C19: 4.7u; 0603
C22: 22p; 0603
C23: 1n; 0603
C25: 10n; 0603
C29: DNI; 0603
D1, D3, D4: BAV19W; SOD123
D2: LM4040; SOT23
H1, H2, H3, H4: MOUNT-HOLE3.2; 3,2
IC1, IC4: AD8226; SO08
IC2, IC3, IC5, IC6: AD825; SO8
R1, R2, R6, R7, R8, R9, R15, R16, R17, R18, R20, R21, R22: 10k; 0603
R3, R14: 1M; 0603
R4, R12, R27: DNI; 0603
R5, R25: 100; 0603
R10: 1k; 0603
R11, R26: 20k; RTRIM3224W
R13: 200; 0603
R19: 5k; 0603
R23, R24: ***; 0603
TP1: TESTPOINT
X1, X2, X5: 22-23-2021
X3: 22-23-2041
X4: 22-23-2061

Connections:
+5V: X3.2, X4.2
GND: C1.2, C2.1, C3.1, C5.2, C6.2, C7.1, C8.2, C9.1, C10.2, C11.1, C12.2, C13.1, C14.2, C15.1, C16.2, C17.1, C18.2, C19.1, C20.2, C21.1, C24.1, C26.2, C27.1, C28.2, C29.2, D2.1 (C), IC1.6 (REF), IC2.3 (IN+), IC3.3 (IN+), IC4.6 (REF), R19.1, R23.2, R24.2, R26.1 (A), TP1.P$1, X2.2, X3.3, X4.5
unnamed: R2.1, X1.2
unnamed: R1.1, X1.1
unnamed: C22.1, C23.1, D1.C, IC3.6 (OUT), R11.1 (A), R11.2 (S)
unnamed: IC1.2 (RG1), R4.1
unnamed: C3.2, C4.1, IC1.1 (-IN), R1.2, R3.1
unnamed: C4.2, C5.1, IC1.4 (+IN), R2.2, R3.2
unnamed: R5.1, X2.1
unnamed: IC1.3 (RG2), R4.2
unnamed: IC2.6 (OUT), R5.2, R6.1
unnamed: IC2.2 (IN-), R6.2, R7.1
unnamed: IC5.3 (IN+), R19.2, R22.1
unnamed: IC4.7 (VOUT), R7.2, R9.2
unnamed: C27.2, R13.1, R18.1
unnamed: IC5.2 (IN-), R17.2, R18.2, R21.1
unnamed: IC1.7 (VOUT), R8.2
unnamed: IC5.6 (OUT), R21.2, R25.1
unnamed: R11.3 (E), R13.2
unnamed: R22.2, X5.2
unnamed: D3.A, D4.C, R25.2, R27.2, X5.1
unnamed: C28.1, D2.2 (A), R20.1, R26.3 (E)
unnamed: R16.1, R24.1, X4.4
unnamed: IC6.3 (IN+), R26.2 (S)
unnamed: IC4.2 (RG1), R12.1
unnamed: IC4.3 (RG2), R12.2
unnamed: C24.2, C25.1, IC4.1 (-IN), R14.1, R15.2
unnamed: C25.2, C26.1, IC4.4 (+IN), R14.2, R16.2
unnamed: R15.1, R23.1, X4.3
unnamed: C29.1, R27.1
unnamed: C23.2, R10.2
unnamed: C22.2, D1.A, IC3.2 (IN-), R8.1, R9.1, R10.1
V+: C1.1, C6.1, C8.1, C10.1, C12.1, C14.1, C16.1, C18.1, C20.1, D3.C, IC1.8 (+VS), IC2.7 (+VS), IC3.7 (+VS), IC4.8 (+VS), IC5.7 (+VS), IC6.7 (+VS), X3.1, X4.1
V-: C2.2, C7.2, C9.2, C11.2, C13.2, C15.2, C17.2, C19.2, C21.2, D4.A, IC1.5 (-VS), IC2.4 (-VS), IC3.4 (-VS), IC4.5 (-VS), IC5.4 (-VS), IC6.4 (-VS), R20.2, X3.4, X4.6
VBIAS: IC6.2 (IN-), IC6.6 (OUT), R17.1

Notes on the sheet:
current control
RF input filter f = 1 / (2*pi*R1*C1)
optional snubber for stability
current monitor
signal
reference
To FET gate source
Rsense or a Hall sensor etc.
Vout < 0 for I > 0
BW adjust
-5V
V > 0 for I > 0
V < 0 for I > 0
set |Vbias| just below FET Vgs threshold
VBIAS < 0


Board: 2 copper layers, 41.9 x 69.8 mm, 76 parts (0 on the bottom side), 35 nets.

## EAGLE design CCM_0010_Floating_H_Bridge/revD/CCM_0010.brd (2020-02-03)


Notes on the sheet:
I_control
top coil
bot coil
This circuit is a floating H-bridge driver initially designed to switch between Helmholtz and anti-Helmholtz configurations in our CaF MOT coils. The power/output stage looks like this, where all 5 N-channel FETs are high current (100A) devices. The H-bridge control needs to float since the drain o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
I_feedback
Using a slightly different configuration, this circuit can be used to easily reverse the both MOT coil currents simultaneously as you might like to do if you want to switch between a red-detuned and blue-detuned MOT and/or molasses. In this configuration the body diodes do the protection for you, t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
A full configuration using 2 of this circuit uses 9 FETs and 2 logic signals to give 4 possibilities: (1) anti-Helmholtz direction 1 (2) anti-Helmholtz direction 2 (3) Helmholtz direction 1 (4) Helmholtz direction 2 This is the most flexible configuration and the body diodes do all the protection f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
The bypass circuit feedback is located on the ground-referenced side for flexibility, using FET driver CCM_0008 or equivalent, and requires using a galvanically isolated current sensor. Note: you can't bypass more current than is flowing through the H-bridge (duh). Unsure how close you can get befo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
coil
bypass
CASR15
+ -
AGND
[B]
protection
diode drop


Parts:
C1, C2, C3, C7, C8, C12, C14, C18: 4.7u; 0603
C4, C5, C6, C9, C10, C11, C13, C17: 0.1u; 0603
C15, C16: 1u; 0603
D1, D2: BAS70; SOT23-3
H1, H2, H3, H4: MOUNT-HOLE3.2; 3,2
IC1: ADUM5230; SO16W
IC2: UAL78L12; SOT89
IC4: HIP4081A; SO20
R1: 10k; 0603
R2, R3: 1k; 0603
R4, R5, R7: 100k; 0603
T1: 2N7002; SOT-23
TP1, TP2: TESTPOINT
X1: 22-23-2041
X2, X3, X4, X5, X6: 22-23-2021

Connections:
+5V: C3.1, C6.1, C7.2, C8.1, C9.2, C10.1, IC1.2 (VDD1-1), IC1.7 (VDD1-2), R1.1, X1.2
+12V: C13.1, C14.1, C17.1, C18.1, D1.1 (A), D2.1 (A), IC1.10 (VDDB), IC2.1 (VO), IC4.2 (BHI), IC4.7 (AHI), IC4.15 (VCC), IC4.16 (VDD), R4.1; also elsewhere on the board
+15V: C1.1, C4.1, X1.1; also elsewhere on the board
-15V: C2.2, C5.2, X1.4; also elsewhere on the board
AGND: C11.2, C12.2, C13.2, C14.2, C17.2, C18.2, IC1.11 (GNDB), IC1.14 (GNDISO), IC2.2 (GND), IC2.2@1 (GND), IC4.3 (DIS), IC4.4 (VSS), IC4.14 (ALS), IC4.17 (BLS), R5.1, R7.1, T1.2 (S), TP1.P$1, X4.2, X5.2; also elsewhere on the board
GND: C1.2, C2.1, C3.2, C4.2, C5.1, C6.2, C7.1, C8.2, C9.1, C10.2, IC1.1 (GND1-1), IC1.4 (GND1-2), IC1.5 (VIA), IC1.8 (GND1-3), TP2.P$1, X1.3, X2.2; also elsewhere on the board
unnamed: IC4.18 (BLO), X4.1
unnamed: IC4.13 (ALO), X5.1
unnamed: IC4.8 (HDEL), R5.2
unnamed: C16.1, D2.3 (C), IC4.10 (AHB)
unnamed: C11.1, C12.1, IC1.15 (VISO), IC2.3 (VI)
unnamed: IC1.9 (VOB), R3.1
unnamed: C16.2, IC4.12 (AHS), X6.2
unnamed: C15.2, D1.3 (C), IC4.1 (BHB)
unnamed: IC4.9 (LDEL), R7.2
unnamed: IC4.5 (BLI), R4.2, T1.1 (D)
unnamed: IC4.6 (ALI), R3.2, T1.3 (G)
unnamed: C15.1, IC4.19 (BHS), X3.2
unnamed: IC4.20 (BHO), X3.1
unnamed: R1.2, R2.1, X2.1
unnamed: IC1.6 (VIB), R2.2
unnamed: IC4.11 (AHO), X6.1

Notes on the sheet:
H-bridge control !A->B! / B->A
12-18V unregulated
high = VISO (unreg)
high = VDDB (reg)
output molex connectors have 1=gate, 2=source
charge pump diodes (D1/D2) should be Schottky (fast), rated for > 60V bootstrap capacitors (C15/C16) should be > 10x FET gate-source capacitance IXFN180N15P FET has Cgs = 7nF IXFN360N10P FET has Cgs = 36nF
nominal ~15 mA isolated current expected quiescent current draw: HIP4081a: 14 mA AD820 (next sheet): 1 mA
BHIGH
BLOW
ALOW
AHIGH
isolated section floating on lower H-bridge source potential (AGND)
section referenced to lab potential (GND)

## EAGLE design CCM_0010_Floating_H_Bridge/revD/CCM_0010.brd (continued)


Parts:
C21, C22, C34: 0.1u; 0603
C28: 47p; 0603
C31: 22p; 0603
C32, C33: DNI; 0603
D4: BAS70; SOT23-3
IC8: HCNR200-300E; DIP8-400
IC9, IC10: AD820; SO08
R6: 10k; 0603
R8, R27: DNI; 0603
R15: 100k; 0603
R20: 6.8k; 0603
R21: 2.2k; 0603
R22: 33k; 0603
R23: 270; 0603
R24: 90k; 0603
R25: 20k; RTRIM3224W
R26: 100; 0603
T2: MMBT3906; SOT23-BEC
X8, X9: 22-23-2021

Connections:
+12V: C34.1, IC10.7 (V+); also elsewhere on the board
+15V: C21.2, IC9.7 (V+), R21.2, R23.2; also elsewhere on the board
-15V: C22.1, IC9.4 (V-), R22.1; also elsewhere on the board
AGND: C32.2, C33.2, C34.2, IC8.5 (A2), IC10.3 (+IN), IC10.4 (V-), X9.2; also elsewhere on the board
GND: C21.1, C22.2, D4.1 (A), IC8.1 (C), IC8.4 (A1), IC9.3 (+IN), R6.1, X8.2; also elsewhere on the board
unnamed: C32.1, IC10.5 (OPT)
unnamed: D4.3 (C), IC8.2 (A), R22.2, T2.C
unnamed: C33.1, R27.1
unnamed: R6.2, R15.1, X8.1
unnamed: C28.2, IC8.3 (C1), IC9.2 (-IN), R15.2
unnamed: R24.2, R25.1 (A)
unnamed: C28.1, IC9.6 (OUT), R20.1
unnamed: R20.2, R21.1, T2.B
unnamed: R23.1, T2.E
unnamed: C31.2, IC8.6 (C2), IC10.2 (-IN), R8.1, R24.1
unnamed: C31.1, IC10.6 (OUT), R8.2, R25.2 (S), R25.3 (E), R26.1
unnamed: R26.2, R27.2, X9.1

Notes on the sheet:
floating on lower H-bridge source potential (receiver)
section referenced to lab potential (transmitter)
adjust for 1:1 optocoupling or install R8 as nominal value (100k) if under feedback
to bypass FET
bypass control from CCM_0008 or equivalent
photocurrent drives IC10 output positive see HCNR200 datasheet circuit #17
optional snubber


Board: 2 copper layers, 50.8 x 76.2 mm, 67 parts (0 on the bottom side), 34 nets.

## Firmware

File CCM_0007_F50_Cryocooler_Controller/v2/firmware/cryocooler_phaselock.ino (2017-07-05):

/*
This project is a Photon-based phase lock for cryocooler-based buffer-gas experiments.
The Gifford-McMahon cryocooler cycle is 1 Hz, with a main compression stroke followed
by a return stroke about 200ms later.  The pulse tubes are a little different, with
a 2 Hz frequency and no discernable return stroke.  Here we detect the sound spikes from
the compression stroke using a microphone placed a couple of mm off the helium line
(near the head works best, the compressor is so loud and causes so much white-noise-like
vibration that it makes things more difficult) and provide digital output signals
for experimental triggering.  An analog input (pin A1, 0-10V) controls the
delay between when a threshold event is detected and when the trigger is pulsed
high.  A variable "dead time" is specified (in ms), triggers cannot be sent more
often than this period.

With no low-pass or high-pass filter components installed, tapping or blowing on
the microphone yields a maximum volume of about 1.5V (the rail).
Placing the microphone near the compressor line yields about 0.6-0.7V.
Background room noise (worst case) is about 0.2-0.3V.
Adjust the threshold as necessary to get reliable triggering.
*/

/*
Decent parameters for different experimental setups:

(1) CaF Gifford-McMahon: the primary cryocooler pulse is very loud and high
pitched, much louder than the secondary pulse that occurs ~ 200 ms later.
threshold = 0.6, deadTime = 900 ms --> 10ms trigger accuracy (probably better than that even)

(2) Neon YbF Gifford-McMahon: the secondary cryocooler pulse seems louder than
the primary one.

(3) He YbF Gifford-McMahon:

(4) Large molecule pulse-tube: overall much quieter but so is the lab
threshold = ?, deadTime = 450 ms
*/

// program constants
const float threshold = 0.6;			// choose a volume threshold, in volts, you can use an oscilloscope to tune
const int deadTime = 900;				// dead time after a pulse before another can be detected (change for different coolers)
const int maxDelay = 1000;				// longest possible delay between high volume and trigger output, corresponds to 10V at BNC input
const float offset = 1.65;				// offset (use if DC coupled - no high-pass filter installed)


#include "application.h"

SYSTEM_MODE(MANUAL);					// run code even if not connected to the cloud

// hardware connections
const int aboveThreshold = D7;			// output, high indicates threshold is currently being exceeded
const int triggerOut = D6;				// pulses high to trigger experiment, on-board led for visual status
const int audioIn = A0;					// microphone output after gain stage and optional filtering
const int delayAdjust = A1;				// analog input for controlling the trigger delay (0-10V divided down to 0-3.3V)
const int volumeIndicator = A3;			// true analog-output for indicating volume

float volume;							// recorded volume level
bool readyForNext = true;				// waiting/ready for next loud trigger event flag


Timer delayTimer(1000, sendTrigger, true);		// timer for delaying trigger output, period adjusted dynamically
Timer deadTimer(deadTime, resetSystem, true);	// timer that resets system to allow next peak to be detected


// this gets called early, before any cloud connectivity etc.
STARTUP(
	WiFi.disconnect();					// don't need a cloud connection for this application
	WiFi.off();							// Photon RGB LED should slowly flash white
)

void setup() {
	pinMode(aboveThreshold, OUTPUT);
	digitalWrite(aboveThreshold, HIGH);		// brief on-board led flash to indicate starting up
	delay(500);
	digitalWrite(aboveThreshold, LOW);
  	pinMode(triggerOut, OUTPUT);
  	digitalWrite(triggerOut, LOW);
}


void loop() {

	volume = (float)(analogRead(audioIn)*3.3/4095);		// read and convert to volts
	volume = abs(volume - offset);

	pinMode(volumeIndicator, OUTPUT);					// for DAC need to continually make an output
	analogWrite(volumeIndicator, 4095*volume/3.3 );		// indicate volume

// if above threshold and trigger isn't active, start the trigger process
	if ( volume > threshold ) {
		digitalWrite(aboveThreshold, HIGH);
		if (readyForNext) {
			readyForNext = false;
			startTimers();
		}
	}
	else {
		digitalWrite(aboveThreshold, LOW);
	}

}


// volume detected an above-threshold event, start the send-trigger timer!
void startTimers() {
	int delayVoltage = analogRead(delayAdjust);					// 0..4095 for 0-3.3V
	int triggerDelay = map(delayVoltage, 0, 4095, 0, maxDelay);	// convert to delay (ms)
	delayTimer.changePeriod(triggerDelay);						// update the timer period for next event
	delayTimer.start();
	deadTimer.start();
}

// send a trigger to start the experiment
void sendTrigger() {
	digitalWrite(triggerOut, HIGH);			// send the trigger to the experiment
	delay(10);
	digitalWrite(triggerOut, LOW);
}

void resetSystem() {
	readyForNext = true;
}

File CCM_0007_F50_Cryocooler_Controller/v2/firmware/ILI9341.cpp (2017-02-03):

/***************************************************
This is an Arduino Library for the Adafruit 2.2" SPI display.
This library works with the Adafruit 2.2" TFT Breakout w/SD card
----> http://www.adafruit.com/products/1480

Check out the links above for our tutorials and wiring diagrams
These displays use SPI to communicate, 4 or 5 pins are required to
interface (RST is optional)
Adafruit invests time and resources providing this open source code,
please support Adafruit and open-source hardware by purchasing
products from Adafruit!

Written by Limor Fried/Ladyada for Adafruit Industries.
MIT license, all text above must be included in any redistribution
****************************************************/

#include "ILI9341.h"
#include <limits.h>
#include "application.h"

// Constructor when using hardware SPI.  Faster, but must use specific SPI pins (http://docs.spark.io/#/hardware):
// A2 : SS(Slave Select)
// A3 : SCK(Serial Clock)
// A4 : MISO(Master In Slave Out)
// A5 : MOSI(Master Out Slave In)
// The other pins are: cs - Chip select (aka slave select), dc - D/C or A0 on the screen (Command/Data switch), rst - Reset
ILI9341::ILI9341(uint8_t rst, uint8_t cs, uint8_t dc, uint8_t bl) : GFX(ILI9341_TFTWIDTH, ILI9341_TFTHEIGHT) {
	_cs = cs;
	_dc = dc;
	_rst = rst;
	_bl = bl;
	_mosi = _sclk = 0;

}

inline void ILI9341::spiwrite(uint8_t c)
{
	SPI.transfer(c);
}

inline void ILI9341::writecommand(uint8_t c)
{
	digitalWrite(_dc, LOW);
	digitalWrite(_sclk, LOW);
	digitalWrite(_cs, LOW);
	spiwrite(c);
	digitalWrite(_cs, HIGH);
}

inline void ILI9341::writedata(uint8_t c)
{
	digitalWrite(_dc, HIGH);
	digitalWrite(_sclk, LOW);
	digitalWrite(_cs, LOW);
	spiwrite(c);
	digitalWrite(_cs, HIGH);
}

// Rather than a bazillion writecommand() and writedata() calls, screen
// initialization commands and arguments are organized in these tables
// stored in PROGMEM.  The table may look bulky, but that's mostly the
// formatting -- storage-wise this is hundreds of bytes more compact
// than the equivalent code.  Companion function follows.
#define DELAY 0x80

// Companion code to the above tables.  Reads and issues
// a series of LCD commands stored in PROGMEM byte array.
void ILI9341::commandList(uint8_t *addr) {

	uint8_t numCommands, numArgs;
	uint16_t ms;

	numCommands = pgm_read_byte(addr++);   // Number of commands to follow
	while (numCommands--) {                 // For each command...
		writecommand(pgm_read_byte(addr++)); //   Read, issue command
		numArgs = pgm_read_byte(addr++);    //   Number of args to follow
		ms = numArgs & DELAY;          //   If hibit set, delay follows args
		numArgs &= ~DELAY;                   //   Mask out delay bit
		while (numArgs--) {                   //   For each argument...
			writedata(pgm_read_byte(addr++));  //     Read, issue argument
		}

		if (ms) {
			ms = pgm_read_byte(addr++); // Read post-command delay time (ms)
			if (ms == 255) {
				ms = 500;     // If 255, delay for 500 ms
			}
			delay(ms);
		}
	}
}

void ILI9341::begin(void) {
	pinMode(_rst, OUTPUT);					// configure I/O pins
	pinMode(_dc, OUTPUT);
	pinMode(_cs, OUTPUT);
	pinMode(_bl,OUTPUT);

	digitalWrite(_rst, LOW);

	mosiport = &_mosi;
	clkport = &_sclk;
	rsport = &_rst;
	csport = &_cs;
	dcport = &_dc;

	SPI.begin();
	SPI.setClockDivider(SPI_CLOCK_DIV2);
	SPI.setBitOrder(MSBFIRST);
	SPI.setDataMode(SPI_MODE0);

	// toggle RST low to reset
	digitalWrite(_rst, HIGH);
	delay(5);
	digitalWrite(_rst, LOW);
	delay(20);
	digitalWrite(_rst, HIGH);
	delay(150);

	writecommand(0xEF);
	writedata(0x03);
	writedata(0x80);
	writedata(0x02);

	writecommand(0xCF);
	writedata(0x00);
	writedata(0XC1);
	writedata(0X30);

	writecommand(0xED);
	writedata(0x64);
	writedata(0x03);
	writedata(0X12);
	writedata(0X81);

	writecommand(0xE8);
	writedata(0x85);
	writedata(0x00);
	writedata(0x78);

	writecommand(0xCB);
	writedata(0x39);
	writedata(0x2C);
	writedata(0x00);
	writedata(0x34);
	writedata(0x02);

	writecommand(0xF7);
	writedata(0x20);

	writecommand(0xEA);
	writedata(0x00);
	writedata(0x00);

	writecommand(ILI9341_PWCTR1);    //Power control
	writedata(0x23);   //VRH[5:0]

	writecommand(ILI9341_PWCTR2);    //Power control
	writedata(0x10);   //SAP[2:0];BT[3:0]

	writecommand(ILI9341_VMCTR1);    //VCM control
	writedata(0x3e);
	writedata(0x28);

	writecommand(ILI9341_VMCTR2);    //VCM control2
	writedata(0x86);  //--

	writecommand(ILI9341_MADCTL);    // Memory Access Control
	writedata(ILI9341_MADCTL_MX | ILI9341_MADCTL_BGR);

	writecommand(ILI9341_PIXFMT);
	writedata(0x55);

	writecommand(ILI9341_FRMCTR1);
	writedata(0x00);
	writedata(0x18);

	writecommand(ILI9341_DFUNCTR);    // Display Function Control
	writedata(0x08);
	writedata(0x82);
	writedata(0x27);

	writecommand(0xF2);    // 3Gamma Function Disable
	writedata(0x00);

	writecommand(ILI9341_GAMMASET);    //Gamma curve selected
	writedata(0x01);

	writecommand(ILI9341_GMCTRP1);    //Set Gamma
	writedata(0x0F);
	writedata(0x31);
	writedata(0x2B);
	writedata(0x0C);
	writedata(0x0E);
	writedata(0x08);
	writedata(0x4E);
	writedata(0xF1);
	writedata(0x37);
	writedata(0x07);
	writedata(0x10);
	writedata(0x03);
	writedata(0x0E);
	writedata(0x09);
	writedata(0x00);

	writecommand(ILI9341_GMCTRN1);    //Set Gamma
	writedata(0x00);
	writedata(0x0E);
	writedata(0x14);
	writedata(0x03);
	writedata(0x11);
	writedata(0x07);
	writedata(0x31);
	writedata(0xC1);
	writedata(0x48);
	writedata(0x08);
	writedata(0x0F);
	writedata(0x0C);
	writedata(0x31);
	writedata(0x36);
	writedata(0x0F);

	writecommand(ILI9341_SLPOUT);    // Exit Sleep
	delay(120);
	writecommand(ILI9341_DISPON);    // Display on

	sleeping = false;
}

bool ILI9341::isAsleep() {return sleeping;}

bool ILI9341::isAwake() {return !sleeping;}

void ILI9341::wakeup() {
	for(uint8_t i = 0 ; i <= backlight; i++) {				// ramp the backlight on
	  analogWrite(_bl,i);
	  delay(1);
	}
	sleeping = false;
}

void ILI9341::sleep() {
	for (uint8_t i=backlight; i==0; i--) {
		analogWrite(_bl,i);
		delay(1);
	}
	sleeping = true;
}

void ILI9341::clearScreen() {fillScreen(background);}

void ILI9341::clearScreen(uint16_t color) {fillScreen(color);}

void ILI9341::showCoordinates(uint16_t x, uint16_t y) {
	drawCircle(x, y, 10, GREEN);
	setCursor(x - 50, y - 30);
	setTextSize(2);
	setTextColor(BLUE);
	print("(");
	print(x);
	print(",");
	print(y);
	print(")");
}

void ILI9341::introScreen() {
	clearScreen();
	fillRect(71, 70, 50, 100, JJCOLOR);
	fillRect(134, 70, 50, 100, JJCOLOR);
	fillRect(197, 70, 50, 100, JJCOLOR);
	drawRect(46, 45, 228, 150, WHITE);
	delay(250);
	drawString(85, 100, "A", WHITE, 5);
	delay(250);
	drawString(147, 100, "c", WHITE, 5);
	delay(250);
	drawString(210, 100, "r", WHITE, 5);
	delay(500);

	clearScreen();
	fillRect(0, 0, 320, 10, JJCOLOR); // status bar
	drawhomeicon(); // draw the home icon
	drawString(1, 1, "Your status bar message here.    JOS 1.3 Beta", WHITE, 1);
	ant(); 											// draw the bas "antenna" line without the "signal waves"
	signal(); 										// draw the "signal waves" around the "antenna"
	homescr(); 										// draw the homescreen
	drawRect(40, 200, 240, 40, WHITE); 				// message box (xo,yo,width,height,color)
	delay(500);
}

// set backlight 0-255
void ILI9341::setBacklight(uint8_t brightness) {
	backlight = brightness;
	analogWrite(_bl, backlight, 500);
}

uint8_t ILI9341::getBacklight() {
	return backlight;
}

void ILI9341::setBackground(uint16_t color) {
	background = color;
	clearScreen();
}

uint16_t ILI9341::getBackground() {
	return background;
}

void ILI9341::drawhomeicon() { // draws a white home icon
	drawLine(280, 219, 299, 200, WHITE);
	drawLine(300, 200, 304, 204, WHITE);
	drawLine(304, 203, 304, 200, WHITE);
	drawLine(305, 200, 307, 200, WHITE);
	drawLine(308, 200, 308, 208, WHITE);
	drawLine(309, 209, 319, 219, WHITE);
	drawLine(281, 219, 283, 219, WHITE);
	drawLine(316, 219, 318, 219, WHITE);
	drawRect(284, 219, 32, 21, WHITE);
	drawRect(295, 225, 10, 15, WHITE);
}

void ILI9341::drawhomeiconred() { // draws a red home icon
	drawLine(280, 219, 299, 200, RED);
	drawLine(300, 200, 304, 204, RED);
	drawLine(304, 203, 304, 200, RED);
	drawLine(305, 200, 307, 200, RED);
	drawLine(308, 200, 308, 208, RED);
	drawLine(309, 209, 319, 219, RED);
	drawLine(281, 219, 283, 219, RED);
	drawLine(316, 219, 318, 219, RED);
	drawRect(284, 219, 32, 21, RED);
	drawRect(295, 225, 10, 15, RED);
}

void ILI9341::signal() { // draws a whit 'signal indicator'
	drawLine((antpos + 4), 4, (antpos + 4), 5, WHITE);
	drawPixel((antpos + 3), 2, WHITE);
	drawPixel((antpos + 3), 7, WHITE);
	drawPixel((antpos + 2), 0, WHITE);
	drawLine((antpos + 2), 3, (antpos + 2), 6, WHITE);
	drawPixel((antpos + 2), 9, WHITE);
	drawPixel((antpos + 1), 1, WHITE);
	drawPixel((antpos + 1), 8, WHITE);
	drawLine(antpos, 2, antpos, 7, WHITE);
	drawLine((antpos + 6), 4, (antpos + 6), 5, WHITE);
	drawPixel((antpos + 7), 2, WHITE);
	drawPixel((antpos + 7), 7, WHITE);
	drawPixel((antpos + 8), 0, WHITE);
	drawLine((antpos + 8), 3, (antpos + 8), 6, WHITE);
	drawPixel((antpos + 8), 9, WHITE);
	drawPixel((antpos + 9), 1, WHITE);
	drawPixel((antpos + 9), 8, WHITE);
	drawLine((antpos + 10), 2, (antpos + 10), 7, WHITE);
}

void ILI9341::ant() {
	fillRect((antpos + 5), 4, 1, 6, WHITE); // draws the "antenna" for the signal indicator
}

void ILI9341::boxes() { // redraw the button outline boxes
	drawRect(0, 20, 150, 50, JJCOLOR);
	drawRect(170, 20, 150, 50, JJCOLOR);
	drawRect(0, 80, 150, 50, JJCOLOR);
	drawRect(170, 80, 150, 50, JJCOLOR);
	drawRect(0, 140, 150, 50, JJCOLOR);
	drawRect(170, 140, 150, 50, JJCOLOR);
}

void ILI9341::homescr() {
	boxes();
	drawString(41, 37, "LEDs", WHITE, 2);
	drawString(210, 37, "Sensors", WHITE, 2);
	drawString(41, 97, "Info", WHITE, 2);
	drawString(210, 97, "Settings", WHITE, 2);
//	drawString(41, 157, "Menu 5", WHITE, 2);
//	drawString(200, 157, "Settings", WHITE, 2);
}
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

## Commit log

2014-03-31 Add Photodiode Amplifier
    This is a photodiode amplifier circuit with about 50kHz bandwidth useful
    for transfer cavity or power monitoring.
    [PDAmpV2.brd, PDAmpV2.sch]
2014-03-31 Add Diode Noise stabilisation circuit
    Add my work in progress circuit to stabilise the noise on a diode laser,
    some more details of the circuit can be found in the "About" document.
    [Lock_in.brd, Lock_in.sch]
2014-04-01 Add Ben's VCO
    This is the standard VCO circuit with an MAT-3 attenuator
    [VCO eagle.brd, VCO eagle.sch]
2014-04-04 Insert 50 ohm resistor into output
    This actually makes the circuit work properly, previously I was doing this
    with a terminator, but that's a bit dangerous for your ICS
    [PDAmpV2.brd, PDAmpV2.sch]
2014-04-14 April 2014 VCO modification
    The proper files for my VCO
    [VCO eagle.brd, VCO eagle.sch]
2014-04-14 Pictures of a slightly older version of circuit
    To get orientation of chokes and amplifiers.
2014-06-01 Add a 50Hz function generator circuit
    [50HzFNGen.brd, 50HzFNGen.sch]
2014-06-01 Some changes to make the function generator board work
    [50HzFNGen.brd, 50HzFNGen.sch]
2014-06-02 finished version of the board
    [50HzFNGen.brd, 50HzFNGen.sch]
2014-06-03 Add a microwave transmission line board at 14.5GHz
    [MicrowaveTransmissionLineBottom.brd, MicrowaveTransmissionLineTop.brd]
2014-06-03 Include boadmaster files for 50Hz FGen
    [50HzFNGen.brd]
2014-06-05 add Longer board
    [MicrowaveTransmissionLineBottomV2.brd, MicrowaveTransmissionLineTopV2.brd]
2014-06-08 New board with taper section
    [MicrowaveTransmissionLineBottomV3.brd, MicrowaveTransmissionLineTopV3.brd]
2014-06-08 A few changes to microwave boards
    [MicrowaveTransmissionLineBottom.brd, MicrowaveTransmissionLineBottomV3.brd, MicrowaveTransmissionLineTop.brd, MicrowaveTransmissionLineTopV3.brd]
2014-06-18 Update to VCO
    I updated the production files, though I didn't see anything wrong with
    them on my computer. It might be an Eagle version problem, so I suggest
    using the .sol .cmp etc directly.
    [VCO eagle.brd, VCO eagle.sch]
2014-07-14 New version of the diode stabliser circuit
    [Lock_in.brd, Lock_in.sch]
2014-09-02 Various new circuits
    Fast photodiode amp
    200V piezo driver
    [CrsHamPreamp.brd, CrsHamPreamp.sch, DectectorPhotodiode.brd, DectectorPhotodiode.sch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]
2015-11-23 adding some circuits to the repo
    [Bipolar_Stepper_Motor_Controller_RevA.brd, Bipolar_Stepper_Motor_Controller_RevA.sch, CCM0004.brd, CCM0004.sch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]
2015-12-17 fixed stepper motor firmware bug with parameter saving (v1.5)
    [CCM0006.brd, CCM0006.sch]
2015-12-17 removing massive stepper motor GUI (full) installer, the partial one should be sufficient
2016-01-13 added resources for updating the firmware of the reflow oven
    [CCM0006.brd, CCM0006.sch]
2016-02-19 Some notes on the commercial VCO board
    The particular problem is that the amplitude adjust driver didn't work. The notes explain a workaround.
2016-04-27 PeizoAmp
    This is the version that was submitted to DirtyPCBs (although that version had a 0 isolate on the top layer, which I fixed here).
    [PiezoAmpHVDCv3.brd]
2016-04-27 Added files via upload
    This is the circuit that was sent to DirtyPCBs
    [PiezoAmpHVDCv3.sch]
2016-04-27 A mistake
    [PiezoAmpHVDCv3.brd]
2016-04-27 Trying to clean up
    Clean up, add Piezo sent to DirtyPCB
    [PiezoAmpHVDCv3.brd, PiezoAmpHVDCv3.sch]
2016-04-27 More cleaning up
    Also added updated library
    [OneInchRound.brd, OneInchRound.sch]
2017-02-03 Added materials for microphone-based cryocooler phase locker.
    [cryocooler_phase_lock.brd, cryocooler_phase_lock.sch]
2017-02-03 CCM_0007: finished initial board layout.
    [cryocooler_phase_lock.brd, cryocooler_phase_lock.sch]
2017-02-07 More work on cryocooler interlock, uploaded ordering files.
    [cryocooler_phase_lock.brd, cryocooler_phase_lock.sch]
2017-03-15 Ben adding FET driver and other bits
    [CA2832 simple.brd, CA2832 simple.sch, EDM switch.GBL, EDM switch.GBO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]
2017-04-10 updating custom parts and FET driver
    [FET sense drive.brd, FET sense drive.sch]
2017-05-02 Finished coil driver controller.
    [coil_driver.brd, coil_driver.sch]
2017-05-10 Added CAD and docs for CCM_0008
    [002.ipt, 002001.ipt, 002002.ipt, 002003.ipt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]
2017-06-26 CCM_0008: added front panel and started output stage design
    [output_stage.brd, output_stage.sch]
2017-08-01 CCM_0008: fixed current monitor schematic wiring error, prototype run current-monitor output will rail if not fixed in hardware.
    [coil_driver.brd, coil_driver.sch]
2017-08-01 CCM_0008: added preliminary output stage design
    [002.ipt, 002001.ipt, 002002.ipt, 002003.ipt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]
2017-08-09 CCM_0007: finished schematic design of v2.
    [F50_cryocooler_controller.brd, F50_cryocooler_controller.sch, cryocooler_phase_lock.brd, cryocooler_phase_lock.sch]
2017-08-14 CCM_0007: finished layout of v2.
    [F50_cryocooler_controller.brd, F50_cryocooler_controller.sch]
2017-08-18 Added CCM_0009: 3-channel precision bipolar current driver.
    [CCM_0009.brd, CCM_0009.sch]
2017-09-05 update to include MPPC files, mainly
    [HV MPPC parts.xlsx, HV MPPC.brd, HV MPPC.sch, July17 S13360-6050VE_data.xlsx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]
2017-10-02 production files for CCM_0009
    [CCM_0009.brd, CCM_0009.sch]
2017-10-02 Initial schematic design of floating H-bridge driver (CCM_0010)
    [CCM_0010.brd, CCM_0010.sch]
2017-10-11 Added production files for CCM_0010
    [CCM_0010.brd, CCM_0010.sch]
2017-10-26 updated custum.lbr, add a few projects
    [OpAmp.brd, OpAmp.sch]
2017-10-30 CCM_0010: component value updates
    [CCM_0010.brd, CCM_0010.sch]
2018-02-01 started design of hardware TCL
    [CCM_0009.brd, CCM_0010.brd, CCM_0010.sch, CCM_0011.brd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]
2018-03-19 Added subrack backplane board, which defines a bus standard for circuits moving forward.
    [CCM_0011.brd, CCM_0011.sch, CCM_0011_Subrack_Backplane.brd, CCM_0011_Subrack_Backplane.sch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]
2018-04-25 Added production materials for subrack backplane (0011).
    [CCM_0011_Subrack_Backplane.GBL, CCM_0011_Subrack_Backplane.GBO, CCM_0011_Subrack_Backplane.GBP, CCM_0011_Subrack_Backplane.GBS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]
2018-05-01 Added preliminary materials for subrack power and HTCL
    [CCM_0012_Subrack_DPWR_And_Mains_Sync.brd, CCM_0012_Subrack_DPWR_And_Mains_Sync.sch, CCM_0014_HTCL.brd, CCM_0014_HTCL.sch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]
2018-05-22 Added laser diode protection circuit
    [CCM_0003.brd, CCM_0003.sch, CCM_0012.brd, CCM_0012.sch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]
2018-05-22 Fixed circuit number conflict~
    [CCM_0016.brd, CCM_0016.sch]
2018-09-06 Shutter driver added.
    [CCM_0009.sch, CCM_0011.brd, CCM_0011.sch, CCM_0012.brd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]
2018-09-19 Added IXFN FET connector board and revB of floating H-bridge driver.
    [CCM_0010.brd, CCM_0010.sch, CCM_0019.brd, CCM_0019.sch]
2018-10-25 Finalized design of revB of CCM_0010. Floating H-bridge now uses a lower power driver, makes it possible to monitor the coil current, and implements an optically isolated bypass option. This latter f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
    [CCM_0010.brd, CCM_0010.sch]
2019-02-01 New leakage monitor files
    [CCM0006.brd, CCM0006.sch, CCM_0003.brd, CCM_0003.sch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]
2019-03-11 Updated designs for MOT coil control and H-bridge switching
    [002.ipt, 002001.ipt, 002002.ipt, 002003.ipt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]
2019-06-13 Updated component values on circuits used for MOT coil driving and H-bridges.
    [CCM_0008.brd, CCM_0008.sch, CCM_0010.brd, CCM_0010.sch]
2019-08-06 Added preliminary designs of CCM_0020, a floating pA leakage current monitor for the new ultracold edm electric-field plates.
    [CCM_0020_receiver.brd, CCM_0020_receiver.sch, CCM_0020_transmitter.brd, CCM_0020_transmitter.sch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]
2019-08-06 Added directories with design resources and descriptions of our all singing all dancing MOT coil control circuits built using CCM_0008 and CCM_0010.
2019-08-06 library update and preliminary design of coil protection circuit
    [CCM_0021.brd, CCM_0021.sch]
2019-08-09 Simplified leakage monitor receiver.
    [CCM_0020_receiver.brd, CCM_0020_receiver.sch]
2019-08-21 CCM_0020 directory organization
    [CCM_0020_transmitter.brd, CCM_0020_transmitter.sch]
2020-02-03 many changes
    [BOM.ods, CCM_0008.brd, CCM_0008.sch, CCM_0009.brd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]
2020-02-05 updates to schematic of CCM_0025, PID
    [CCM_0025.brd, CCM_0025.sch]
2020-02-10 Finished layout design of CCM_0020_revC
    [CCM_0020_revC.brd, CCM_0020_revC.sch]
